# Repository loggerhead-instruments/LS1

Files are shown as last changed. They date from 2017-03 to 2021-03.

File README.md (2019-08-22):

# LS1
LS1 Snap multi-card audio recorder

## Updating Firmware

1.	Install Teensyduino from https://www.pjrc.com/teensy/loader.html
2.	Get latest hex file from appropriate repository
	https://github.com/loggerhead-instruments/LS1/blob/master/hex/LS1.2019-04-12.hex
	To download the file, right click on the Raw button and select Save As link.
3.	Connect microUSB cable to small board on bottom of main LS1 board. You may need to unscrew it. The microUSB cable will provide power to the LS1.
4.	Run the Teensy Loader program.
5.	From File Menu, select Open HEX File. Note that you may get an error saying the hex file is too large. You can ignore this message.
6.	From Operation menu, select Program (you may have to turn off automatic mode). Note you may need to do a physical reset by removing the board and shorting (connect with a paper clip or forceps) the pins circled in red.
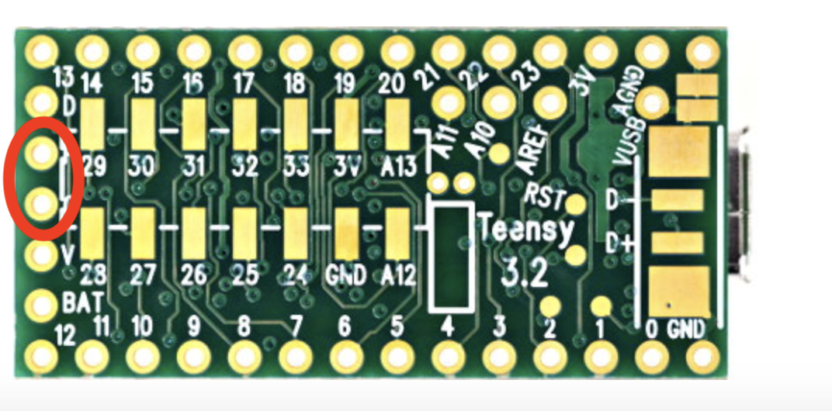
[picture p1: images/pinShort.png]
Teensy reset


To check whether the firmware has been updated, collect some data, and check the log files for the version date of the firmware.

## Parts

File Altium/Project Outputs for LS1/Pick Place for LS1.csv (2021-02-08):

Designator | Comment | Layer | Footprint | Center-Y(mm) | Center-X(mm) |  |  |  |  | X | Y | Rotation | Description
C40 | 0.01uF | BottomLayer | 402 | -50.292 | 65.913 | -27.3 | 10.6 | -27.317 | 10.584 |  |  | 270 | Ceramic Chip Capacitor - Standard
C39 | 0.01uF | BottomLayer | 402 | -14.986 | 9.652 |  |  | -62.623 | 66.845 |  |  | 360 | Ceramic Chip Capacitor - Standard
C36 | 0.01uF | BottomLayer | 402 | -34.798 | 28.702 |  |  | -42.811 | 47.795 |  |  | 360 | Ceramic Chip Capacitor - Standard
C6 | 0.01uF | BottomLayer | 402 | -37.465 | 68.326 |  |  | -40.144 | 8.171 |  |  | 270 | Ceramic Chip Capacitor - Standard
C37 | 0.1uF | BottomLayer | 402 | -50.292 | 63.881 |  |  | -27.317 | 12.616 |  |  | 270 | Ceramic Chip Capacitor - Standard
C33 | 0.1uF | BottomLayer | 402 | -17.018 | 9.652 |  |  | -60.591 | 66.845 |  |  | 360 | Ceramic Chip Capacitor - Standard
C30 | 0.1uF | BottomLayer | 402 | -36.703 | 28.702 |  |  | -40.906 | 47.795 |  |  | 360 | Ceramic Chip Capacitor - Standard
C2 | 0.1uF | BottomLayer | 402 | -37.719 | 66.421 |  |  | -39.89 | 10.076 |  |  | 270 | Ceramic Chip Capacitor - Standard
C35 | 10uF | BottomLayer | Tant0805 | -50.419 | 62.357 |  |  | -27.19 | 14.14 |  |  | 90
C31 | 10uF | BottomLayer | Tant0805 | -18.542 | 9.652 |  |  | -59.067 | 66.845 |  |  | 180
C29 | 10uF | BottomLayer | Tant0805 | -38.481 | 28.702 |  |  | -39.128 | 47.795 |  |  | 180
C1 | 10uF | BottomLayer | Tant0805 | -37.846 | 64.77 |  |  | -39.763 | 11.727 |  |  | 90
C38 | 1uF | BottomLayer | 402 | -42.799 | 64.008 |  |  | -34.81 | 12.489 |  |  | 90 | Ceramic Chip Capacitor - Standard
C34 | 1uF | BottomLayer | 402 | -16.764 | 3.175 |  |  | -60.845 | 73.322 |  |  | 90 | Ceramic Chip Capacitor - Standard
C32 | 1uF | BottomLayer | 402 | -36.322 | 22.479 |  |  | -41.287 | 54.018 |  |  | 90 | Ceramic Chip Capacitor - Standard
C4 | 1uF | BottomLayer | 402 | -31.242 | 66.421 |  |  | -46.367 | 10.076 |  |  | 360 | Ceramic Chip Capacitor - Standard
P24 | CoinCellHolder | BottomLayer | CoinCellHolder | -36.785 | 9.652 |  |  |  |  |  |  | 90
U10 | DS3231 | BottomLayer | DS3231 | -4.318 | 10.4 |  |  |  |  |  |  | 360
U9 | LP3985IM5-3.3 | BottomLayer | MF05A_N | -46.609 | 64.897 | -31 | 11.6 | -77.609 | 76.497 |  |  | 270 | Micropower, 150mA Low-Noise Ultra Low-Dropout CMOS Voltage Regulator
U8 | LP3985IM5-3.3 | BottomLayer | MF05A_N | -16.002 | 6.096 | -61.8 | 70.2 | -77.802 | 76.296 |  |  | 360 | Micropower, 150mA Low-Noise Ultra Low-Dropout CMOS Voltage Regulator
U7 | LP3985IM5-3.3 | BottomLayer | MF05A_N | -35.687 | 25.273 |  |  |  |  |  |  | 360 | Micropower, 150mA Low-Noise Ultra Low-Dropout CMOS Voltage Regulator
U1 | LP3985IM5-3.3 | BottomLayer | MF05A_N | -34.036 | 67.31 |  |  |  |  |  |  | 270 | Micropower, 150mA Low-Noise Ultra Low-Dropout CMOS Voltage Regulator
 | Header 2 | TopLayer | HDR1X2 | -63.881 | 16.891 |  |  |  |  |  |  | 180 | Header, 2-Pin
 | Header 2 | TopLayer | HDR1X2 | -61.595 | 23.368 |  |  |  |  |  |  | 180 | Header, 2-Pin
 | HYDROPHONE_MON | TopLayer | HDR1X3 | -58.674 | 31.369 |  |  |  |  |  |  | 180 | Header, 3-Pin
CAL | MJ1-3510-SMT | TopLayer | CUI_MJ1-3510-SMT | -78.197 | 8.643 |  |  |  |  |  |  | 0 | 3.5 mm, Mono, Right Angle, Surface Mount (SMT), Audio Jack Connector
R10 | 10k | TopLayer | 3-0603 | -24.765 | 17.907 |  |  |  |  |  |  | 180 | Precision Thick Film Chip Resistor, 10 Ohm to 1M Ohm Range, 1% and 0.5% Tolerance, 0603 Size, 0.063 W
R9 | 10k | TopLayer | 3-0603 | -29.718 | 18.288 |  |  |  |  |  |  | 180 | Precision Thick Film Chip Resistor, 10 Ohm to 1M Ohm Range, 1% and 0.5% Tolerance, 0603 Size, 0.063 W
R8 | 10k | TopLayer | 3-0603 | -11.303 | 9.525 |  |  |  |  |  |  | 180 | Precision Thick Film Chip Resistor, 10 Ohm to 1M Ohm Range, 1% and 0.5% Tolerance, 0603 Size, 0.063 W
R7 | 0X | TopLayer | 3-0603 | -57.023 | 15.367 |  |  |  |  |  |  | 360 | Precision Thick Film Chip Resistor, 10 Ohm to 1M Ohm Range, 1% and 0.5% Tolerance, 0603 Size, 0.063 W
P25 | Header 2 | TopLayer | HDR1X2 | -9.652 | 47.752 |  |  |  |  |  |  | 180 | Header, 2-Pin
P19 | microUSB | TopLayer | microUSB-B | -7.661 | 69.444 |  |  |  |  |  |  | 90
P18 | Header 3 | TopLayer | HDR1X3 | -79.339 | 56.4388 |  |  |  |  |  |  | 90 | Header, 3-Pin
C28 | 1.0uF | TopLayer | 402 | -67.528 | 42.47 |  |  |  |  |  |  | 360 | Ceramic Chip Capacitor - Standard
C27 | 1.0uF | TopLayer | 402 | -66.258 | 42.47 |  |  |  |  |  |  | 360 | Ceramic Chip Capacitor - Standard
U6 | MCP1700T-1802E/TT | TopLayer | SOT-23-TT3_N | -57.622 | 43.867 |  |  |  |  |  |  | 180 | Low Quiescent Current LDO, 3-Pin SOT-23, Extended Temperature, Tape and Reel
U5 | LP3985IM5-3.3 | TopLayer | MF05A_N | -63.591 | 59.996 |  |  |  |  |  |  | 180 | Micropower, 150mA Low-Noise Ultra Low-Dropout CMOS Voltage Regulator
U4 | LP3985IM5-3.3 | TopLayer | MF05A_N | -58.13 | 20.626 |  |  |  |  |  |  | 0 | Micropower, 150mA Low-Noise Ultra Low-Dropout CMOS Voltage Regulator
U3 | SGTL5000 | TopLayer | QFN32 | -62.829 | 49.709 |  |  |  |  |  |  | 360 | SGTL5000
U2 | LP3985IM5-3.3 | TopLayer | MF05A_N | -78.196 | 42.216 |  |  |  |  |  |  | 0 | Micropower, 150mA Low-Noise Ultra Low-Dropout CMOS Voltage Regulator
R6 | 10k | TopLayer | 3-0603 | -29.682 | 40.692 |  |  |  |  |  |  | 90 | Precision Thick Film Chip Resistor, 10 Ohm to 1M Ohm Range, 1% and 0.5% Tolerance, 0603 Size, 0.063 W
R5 | 10k | TopLayer | 3-0603 | -28.158 | 44.375 |  |  |  |  |  |  | 0 | Precision Thick Film Chip Resistor, 10 Ohm to 1M Ohm Range, 1% and 0.5% Tolerance, 0603 Size, 0.063 W
R4 | 10k | TopLayer | 3-0603 | -42.509 | 55.424 |  |  |  |  |  |  | 270 | Precision Thick Film Chip Resistor, 10 Ohm to 1M Ohm Range, 1% and 0.5% Tolerance, 0603 Size, 0.063 W
R3 | 10k | TopLayer | 3-0603 | -40.731 | 38.66 |  |  |  |  |  |  | 180 | Precision Thick Film Chip Resistor, 10 Ohm to 1M Ohm Range, 1% and 0.5% Tolerance, 0603 Size, 0.063 W
R2 | 100k | TopLayer | 3-0603 | -38.608 | 54.356 |  |  |  |  |  |  | 180 | Precision Thick Film Chip Resistor, 10 Ohm to 1M Ohm Range, 1% and 0.5% Tolerance, 0603 Size, 0.063 W
R1 | 100k | TopLayer | 3-0603 | -37.084 | 54.356 |  |  |  |  |  |  | 0 | Precision Thick Film Chip Resistor, 10 Ohm to 1M Ohm Range, 1% and 0.5% Tolerance, 0603 Size, 0.063 W
P17 | HYDROPHONE | TopLayer | HDR1X3 | -61.432 | 41.581 |  |  |  |  |  |  | 180 | Header, 3-Pin
P16 | HYDROPHONE | TopLayer | HDR1X3 | -61.468 | 31.369 |  |  |  |  |  |  | 180 | Header, 3-Pin
P15 | pushbutton | TopLayer | SOP4 | -18.851 | 26.573 |  |  |  |  |  |  | 0
P14 | pushbutton | TopLayer | SOP4 | -27.868 | 26.573 |  |  |  |  |  |  | 0
P13 | pushbutton | TopLayer | SOP4 | -9.707 | 26.573 |  |  |  |  |  |  | 0
P12 | Header 2 | TopLayer | HDR1X2 | -68.834 | 3.556 |  |  |  |  |  |  | 180 | Header, 2-Pin
P11 | Header 4 | TopLayer | HDR1X4 | -47.208 | 20.372 |  |  |  |  |  |  | 90 | Header, 4-Pin
P10 | Header 6 | TopLayer | HDR1X6 | -8.981 | 1.068 |  |  |  |  |  |  | 90 | Header, 6-Pin
P9 | BIG CAP 1000 uF | TopLayer | HDR1X3 | -22.098 | 15.748 |  |  |  |  |  |  | 360 | Header, 3-Pin
P8 | BIG CAP 1000 uF | TopLayer | HDR1X3 | -3.429 | 27.178 |  |  |  |  |  |  | 360 | Header, 3-Pin
P7 | microSD Hirose | TopLayer | DM3D_microSD | -48.7955 | 6.328 |  |  |  |  |  |  | 360
P6 | microSD Hirose | TopLayer | DM3D_microSD | -32.4125 | 6.328 |  |  |  |  |  |  | 360
P5 | microSD Hirose | TopLayer | DM3D_microSD | -49.5575 | 65.658 |  |  |  |  |  |  | 180
P4 | microSD Hirose | TopLayer | DM3D_microSD | -33.0475 | 65.658 |  |  |  |  |  |  | 180
P3 | Header 2 | TopLayer | HDR1X2 | -9.652 | 39.243 |  |  |  |  |  |  | 180 | Header, 2-Pin
P2 | switch | TopLayer | HDR1X3 | -0.345 | 27.23 |  |  |  |  |  |  | 180 | Header, 3-Pin
P1 | Teensy3.x | TopLayer | Teensy3.x | -29.301 | 42.597 |  |  |  |  |  |  | 180
C26 | 1uF | TopLayer | 402 | -58.13 | 41.454 |  |  |  |  |  |  | 270 | Ceramic Chip Capacitor - Standard
C25 | 10uF | TopLayer | Tant0805 | -57.749 | 47.931 |  |  |  |  |  |  | 90
C24 | 1.0uF | TopLayer | 402 | -64.099 | 35.993 |  |  |  |  |  |  | 270 | Ceramic Chip Capacitor - Standard
C23 | 1.0uF | TopLayer | 402 | -68.29 | 35.993 |  |  |  |  |  |  | 270 | Ceramic Chip Capacitor - Standard
C22 | 0.01uF | TopLayer | 402 | -60.924 | 58.218 |  |  |  |  |  |  | 180 | Ceramic Chip Capacitor - Standard
C21 | 1uF | TopLayer | 402 | -63.845 | 62.79 |  |  |  |  |  |  | 90 | Ceramic Chip Capacitor - Standard
C20 | 0.1uF | TopLayer | 402 | -63.718 | 57.075 |  |  |  |  |  |  | 90 | Ceramic Chip Capacitor - Standard
C19 | 10uF | TopLayer | Tant0805 | -63.718 | 55.551 |  |  |  |  |  |  | 270
C18 | 0.1uF | TopLayer | 402 | -66.639 | 47.027 |  |  |  |  |  |  | 180 | Ceramic Chip Capacitor - Standard
C17 | 0.01uF | TopLayer | 402 | -59.436 | 24.384 |  |  |  |  |  |  | 360 | Ceramic Chip Capacitor - Standard
C16 | 0.1uF | TopLayer | 402 | -63.591 | 54.154 |  |  |  |  |  |  | 90 | Ceramic Chip Capacitor - Standard
C15 | 1uF | TopLayer | 402 | -57.749 | 17.832 |  |  |  |  |  |  | 270 | Ceramic Chip Capacitor - Standard
C14 | 0.1uF | TopLayer | 402 | -57.404 | 23.368 |  |  |  |  |  |  | 270 | Ceramic Chip Capacitor - Standard
C13 | 10uF | TopLayer | Tant0805 | -57.404 | 25.019 |  |  |  |  |  |  | 90
C12 | 0.1uF | TopLayer | 402 | -62.448 | 46.026 |  |  |  |  |  |  | 90 | Ceramic Chip Capacitor - Standard
C11 | 0.01uF | TopLayer | 402 | -80.609 | 44.375 |  |  |  |  |  |  | 360 | Ceramic Chip Capacitor - Standard
C10 | 1uF | TopLayer | 402 | -77.942 | 39.422 |  |  |  |  |  |  | 270 | Ceramic Chip Capacitor - Standard
C9 | 0.1uF | TopLayer | 402 | -77.815 | 44.883 |  |  |  |  |  |  | 270 | Ceramic Chip Capacitor - Standard
C8 | 10uF | TopLayer | Tant0805 | -77.815 | 46.28 |  |  |  |  |  |  | 90
C7 | 0.1uF | TopLayer | 402 | -57.749 | 46.534 |  |  |  |  |  |  | 270 | Ceramic Chip Capacitor - Standard
C5 | 0.1uF | TopLayer | 402 | -5.044 | 19.61 |  |  |  |  |  |  | 180 | Ceramic Chip Capacitor - Standard
C3 | 10uF | TopLayer | Tant0805 | -3.647 | 19.61 |  |  |  |  |  |  | 0
P20 | 1x4 1.27mm | TopLayer | Header1x4_1.27mm | -50.038 | 27.051 |  |  |  |  |  |  | 360
P21 | 1x4 1.27mm | TopLayer | Header1x4_1.27mm | -44.069 | 31.115 |  |  |  |  |  |  | 90
P22 | 1x4 1.27mm | TopLayer | Header1x4_1.27mm | -44.069 | 23.368 |  |  |  |  |  |  | 90
P23 | 1x4 1.27mm | TopLayer | Header1x4_1.27mm | -44.069 | 27.305 |  |  |  |  |  |  | 90

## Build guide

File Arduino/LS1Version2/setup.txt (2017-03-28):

// Example setup.txt file

// Set time on power
TM 2016-06-06 12:00:00

// Enable IMU 100 Hz
IM 100.0

// MS Pressure
MP

// RGB light sensor
LS

// Rec duration
RD 30

// Rec interval
RI 30

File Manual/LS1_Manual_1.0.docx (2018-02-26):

# LS1/LS1X MANUAL

Multi-card Long-Term Underwater Acoustic Recorder

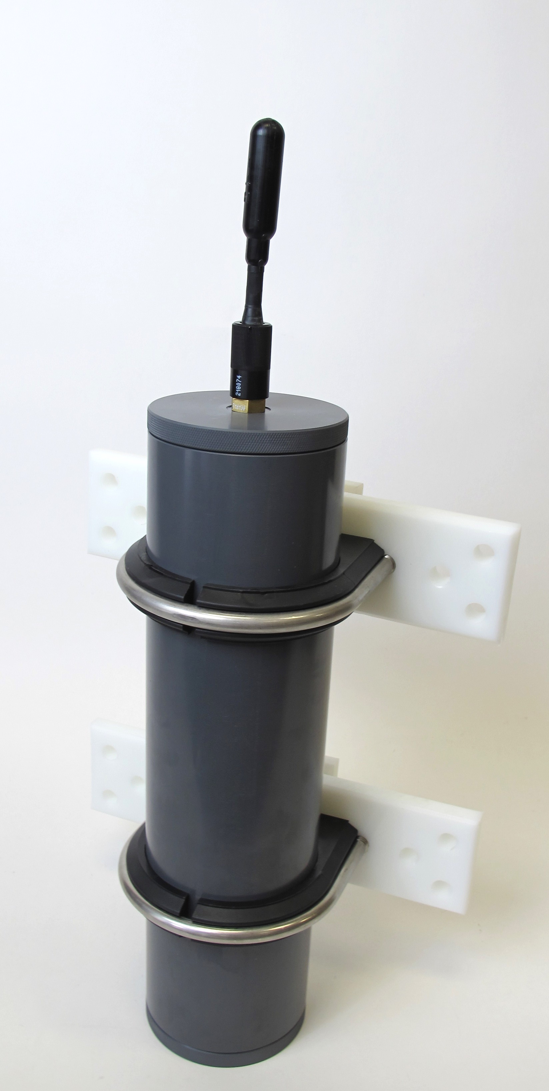
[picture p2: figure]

Manual v1.0

Updated 26 February 2018

www.loggerhead.com

# Overview

Hardware

LS1/LS1X is a multi-card datalogger designed for collecting large amounts of underwater acoustic recordings. Setup is designed to run through a simple button interface with a display. No PC is needed to setup and deploy the LS1/LS1X.

- HTI-96-min hydrophone
- Fixed 44.1 kHz sample rate
- Up to 4 microSD cards formatted as FAT32

Software

LS1/LS1X store data directly as audio wav files.

Any audio analysis software (Adobe Audition, Cornell Raven, MATLAB, R, Python) will work with these files.

Setting up LS1/LS1X for Deployment

See the online video for a tutorial on setting up the LS1/LS1X

Step 1. Prepare microSD card. Create setup.txt file if changing default gain setting. This is usually not necessary. Be sure to safely eject the card before removing from computer.

microSD cards larger than 32 GB need to be formatted as FAT32. Appendix 1 describes software that can be used to do this on Windows PCs.

Step 2. O-rings. Clean and grease o-rings with silicone grease and insert into the groove on the ring. The fatter radial o-ring is 5 mm wide x 90 mm inner diameter (McMaster Part number 9262K395 (https://www.mcmaster.com/)). The o-ring that seals with the top of the tube is -155 (McMaster Part number 9452K176 (https://www.mcmaster.com/)).

Step 3. Turn on power switch.

The microSD cards will be scanned for free memory. There MUST be a card in slot 1.

Use buttons to change settings

Enter: Used to move through menu settings and accept changes.

UP/DN: Used to change values.

Display Setting | Description
UP+DN->Rec | Hold down UP + DN to start Press Enter to change settings
Rec: | Record duration in seconds
Slp: | Sleep duration in seconds. This is the time from the END of one recording to the START of the next recording.
Batt: | Number of battery packs you will fill. There are 3 D-cells per battery pack. This setting was made available in Feb 2018. Previous versions of firmware used 4 battery packs for this setting.
Year: | Year
Month: | Month
Day: | Day of month
Hour: | Hour (24 hour time)
Minute: | Minute
Second: | Second
Mode: | Switch between Norm(al) and Diel recording. In Diel recording mode the Start HH:MM and End HH:MM are specified to limit recording to certain parts of the day (e.g. record only in the morning). In Normal recording mode, recordings are made throughout the day.

Step 5. Start Recording. Hold down the UP and DN buttons at the same time to start recording. If this is not done, the recorder will automatically start after 15 minutes.

Step 6. Close lid. Lids should be closed securely using a coin. It should be more than hand-tight.

setup.txt Commands

All commands are optional. Default column lists values if no setting in setup.txt file. Record duration and record interval can be set through the button interface.

Command | Function | Default | Example | Setup.txt example
RD | Record duration (s) | Last used | Record 600 second files | RD 600
RI | Record interval (s) | Last used | Sleep 240 seconds between files | RI 240
SG | Hydrophone system gain. See table for dB gains associated with different settings. | 4 | Set gain to setting ‘10’, which corresponds to 11.1 dB gain | SG 10
ND | Remove DC from audio. Turning on increases electrical noise | Off | Turn on feature to remove DC from audio | ND

Power

The LS1 has battery holders for 4 sets of D-cell batteries (12 batteries total).

The LS1X has battery holders for 8 sets of D-cell batteries (24 batteries total).

Always use new batteries with the LS1, and tape them into place.

The display will provide estimated run time based on the number of battery packs that are filled (LS1: 1-4 battery packs: LS1X: 1-8 battery packs) and the memory available in all of the microSD cards.

# HTI Hydrophone and Recording Gain

The LS1/LS1X uses a hydrophone manufactured by High-Tech Inc. The sensitivity of the hydrophone will be on a specification sheet included with the shipment (typically -170 dBV/uPa or -180 dBV/uPa).

The hydrophone has a red LED in the end to indicate when it is getting power. This will only be turned on during startup and recording. The hydrophone red LED will be off when sleeping.

The A/D converter gain can be changed through the setup.txt file. The default is setting 4. The setting can be changed with SG command in setup.txt. The actual setting that was used is stored to the log.txt file.

Setting | Clip Level (peak-peak) | Clip Level (peak) | Gain (dB)
0 | 3.12 | 1.56 | -3.9
1 | 2.63 | 1.315 | -2.4
2 | 2.22 | 1.11 | -0.9
3 | 1.87 | 0.935 | 0.6
4 | 1.58 | 0.79 | 2.0
5 | 1.33 | 0.665 | 3.5
6 | 1.11 | 0.555 | 5.1
7 | 0.94 | 0.47 | 6.6
8 | 0.79 | 0.395 | 8.1
9 | 0.67 | 0.335 | 9.5
10 | 0.56 | 0.28 | 11.1
11 | 0.48 | 0.24 | 12.4
12 | 0.4 | 0.2 | 14.0
13 | 0.34 | 0.17 | 15.4
14 | 0.29 | 0.145 | 16.8
15 | 0.24 | 0.12 | 18.4

Vent Plug

This plug is only to be used if there is a leak in the housing.

A leak in the housing can be dangerous because the housing will pressurize internally to the same pressure as the depth of deployment.

If there is a leak, it is critical to relieve the pressure before removing the lid, otherwise the lid could fly off.

The vent plug can be used to relieve the pressure, by turning it slowly until you start hearing air come out. Once air starts coming out, stop unscrewing and wait until air stops coming out. The vent plug is designed to stay in the endcap and safely vent air through holes machined in the plug.

Once the internal pressure has equalized, you may remove the top lid with the hydrophone. There is no need to fully remove the vent plug. Then gently retighten the vent plug. On PVC housings be very careful not to overtighten the plug, otherwise the threads in the bottom endcap may strip.

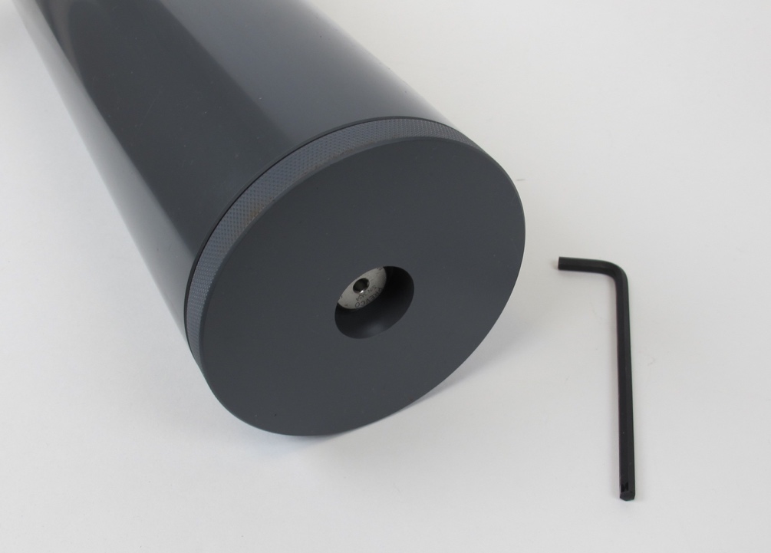
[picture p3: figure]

# Appendix I

Formatting SD card with EaseUS Partition Master for Cards Larger than 32 GB

32 GB cards can be formatted as FAT32 in Windows with standard re-formatting. New 32 GB cards will come formatted as FAT32 (you don’t need to do anything).

Cards larger than 32 GB can not be formatted with the FAT32 file system with the regular windows formatting tools. Cards shipped from Loggerhead have been formatted as FAT32. The exFAT file system will not work with the DSG boards. These larger cards can be formatted with EaseUS Partition Master, which has a free personal edition available.

http://www.partition-tool.com/personal.htm

Run EaseUS Partition Master

1. Select drive with SD card.

2. Click on Format Partition on left.

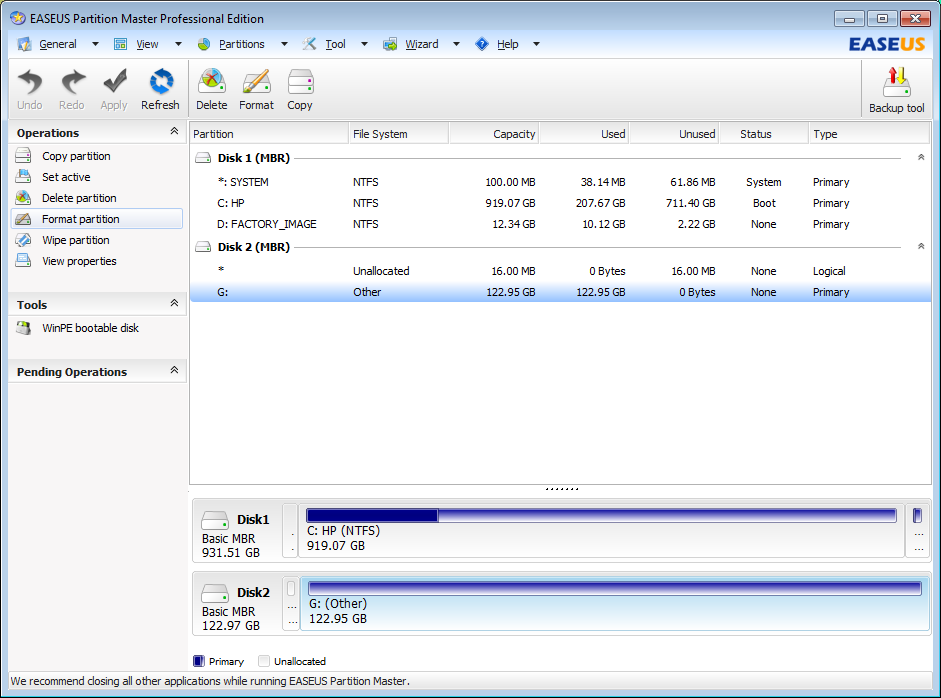
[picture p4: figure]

3. Make sure File System is FAT32. Click OK.

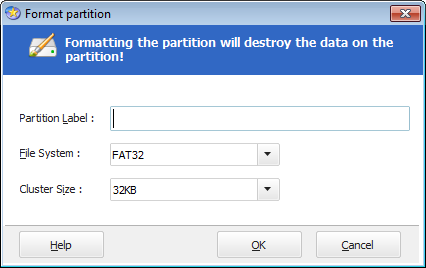
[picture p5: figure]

4. Click Apply on the toolbar. Then click Yes.

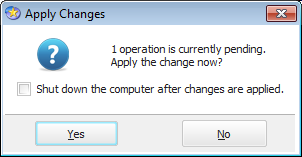
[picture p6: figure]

You should see this screen. When it is done you can close EaseUS.

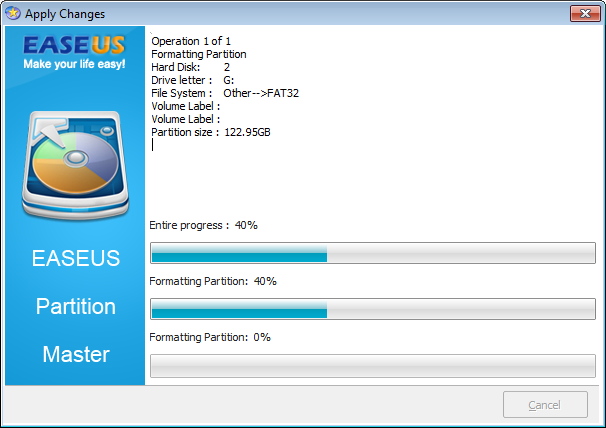
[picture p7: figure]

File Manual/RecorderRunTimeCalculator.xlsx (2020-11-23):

Record Duration (s) | Sleep Duration (s) | Sample Rate | Period (s) | Duty cycle | mA Record | mA Sleep | mAh per battery pack | battery packs | total power | Avg Power Consumption (mA) | Power Duration (h) | Power Duration (Days) | Record Duration (h) | Memory (MB) | Memory (GB)
300 | 600 | 96000 | 900 | 0.3333333333 | 50 | 3.7 | 12000 | 8 | 96000 | 19.13333333 | 5017.421603 | 209.0592334 | 1672.473868 | 1156013.937 | 1156.013937

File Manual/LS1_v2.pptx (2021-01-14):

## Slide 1

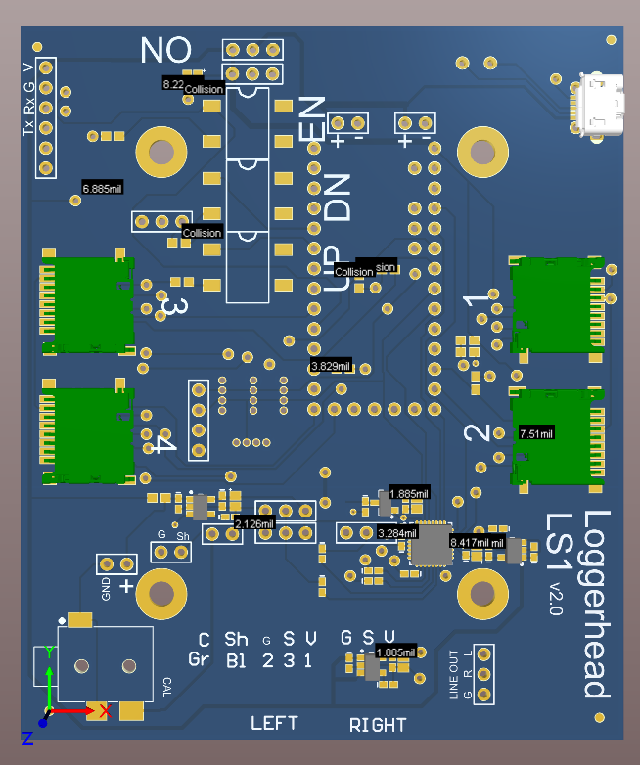
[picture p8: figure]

4

6

2

3

5

1

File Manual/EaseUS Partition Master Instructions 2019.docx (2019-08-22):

EaseUS Partition Master Instructions

https://www.easeus.com/download/epmf-download.html

1. Click on the drive with the microSD card.
2. Click Format button the right
3. In pop-up dialog box Change cluster size to 64 KB. Click OK
4. On top of screen click on Execute 1 Operation

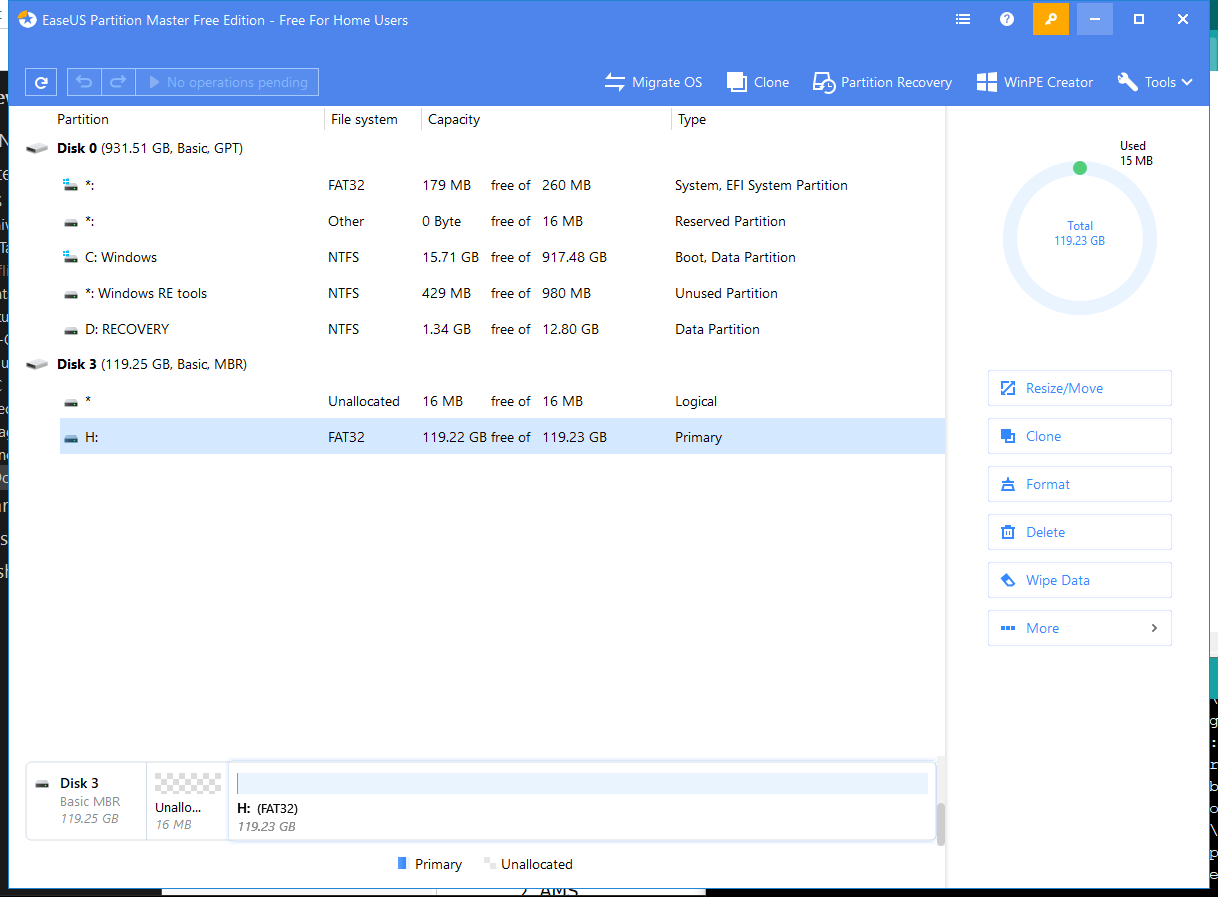
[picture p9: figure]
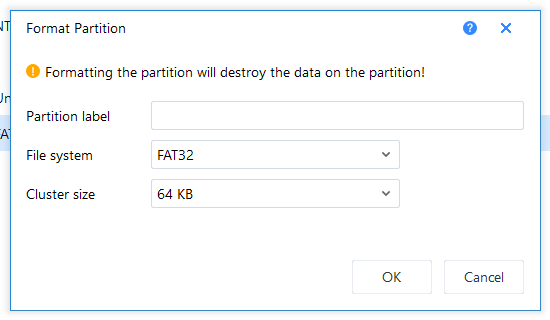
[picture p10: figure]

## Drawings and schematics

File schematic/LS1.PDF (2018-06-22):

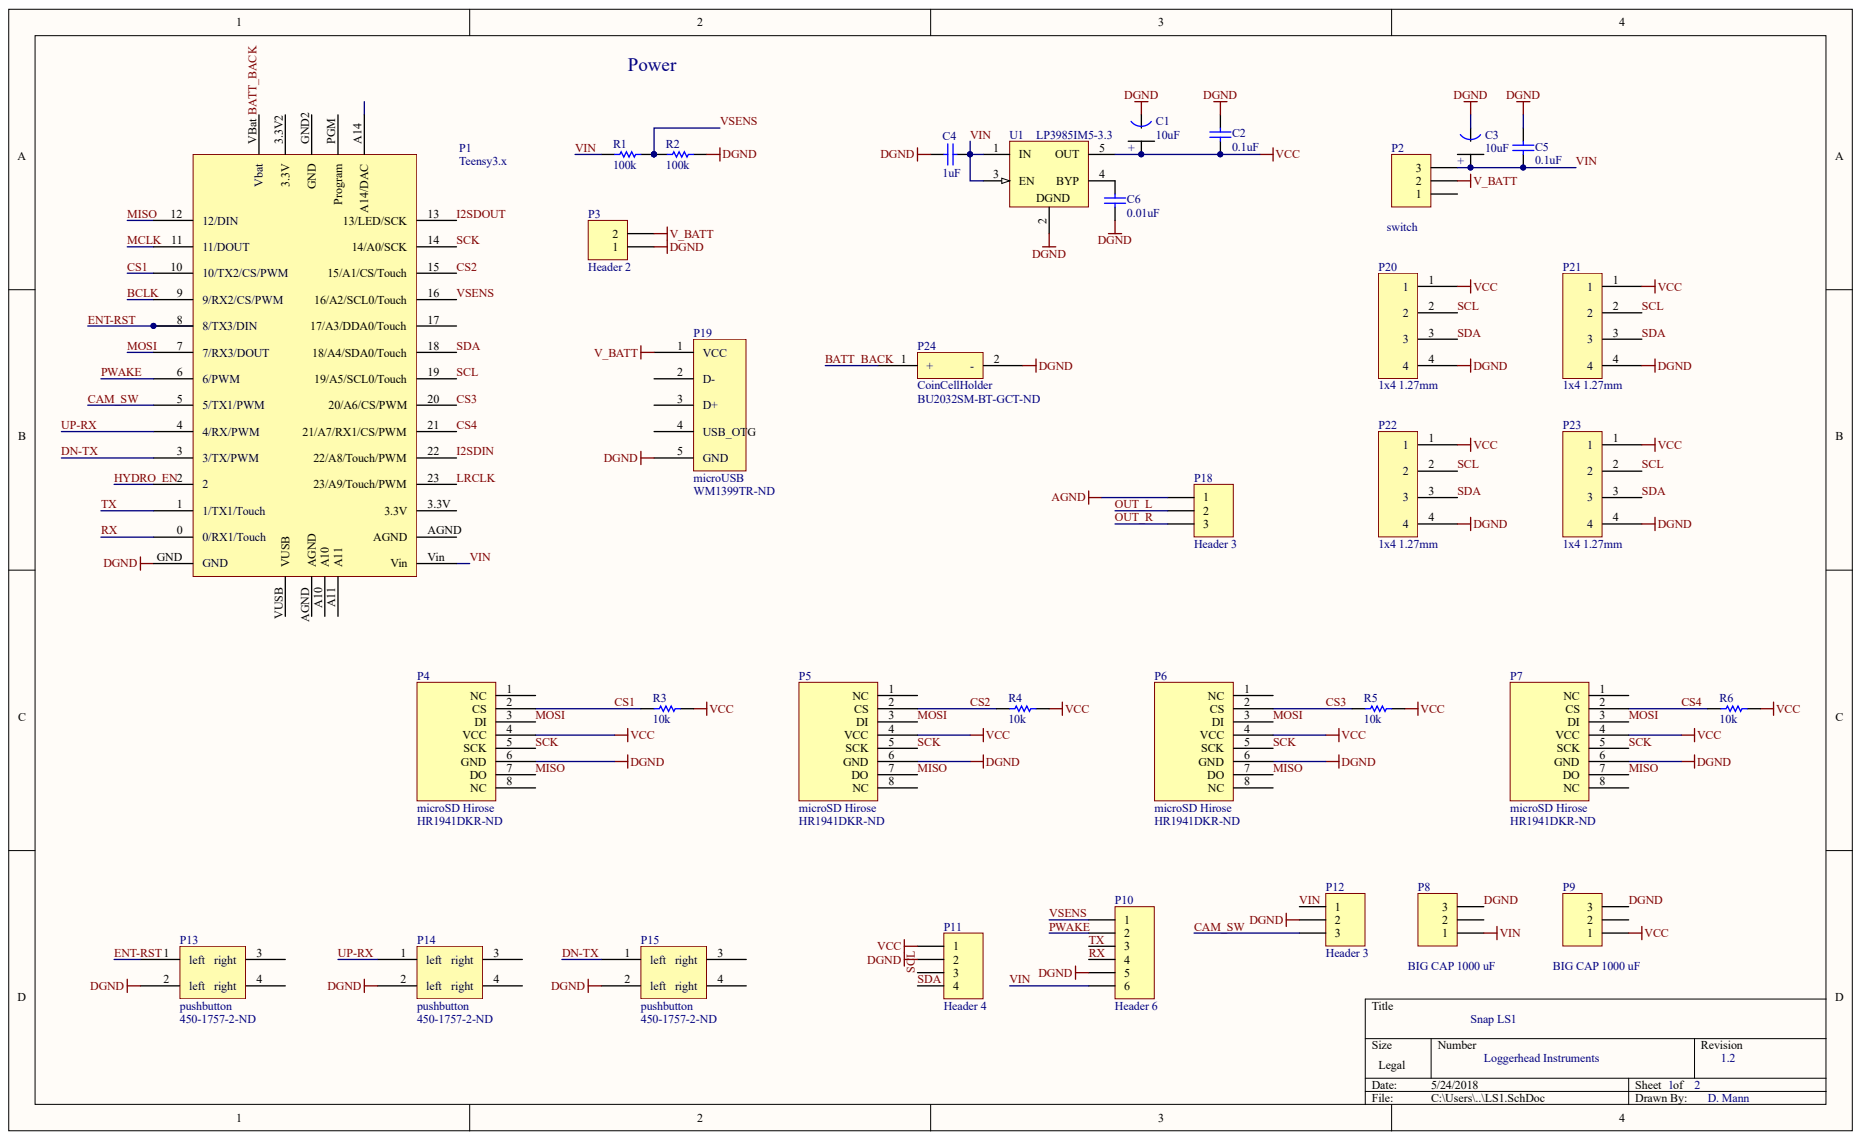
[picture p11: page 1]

Size Legal | Number Loggerhead Instruments | Revision 1.2

Date: 5/24/2018 | Sheet of 1 2
File: C:\Users\..\LS1.SchDoc | Drawn By: D. Mann

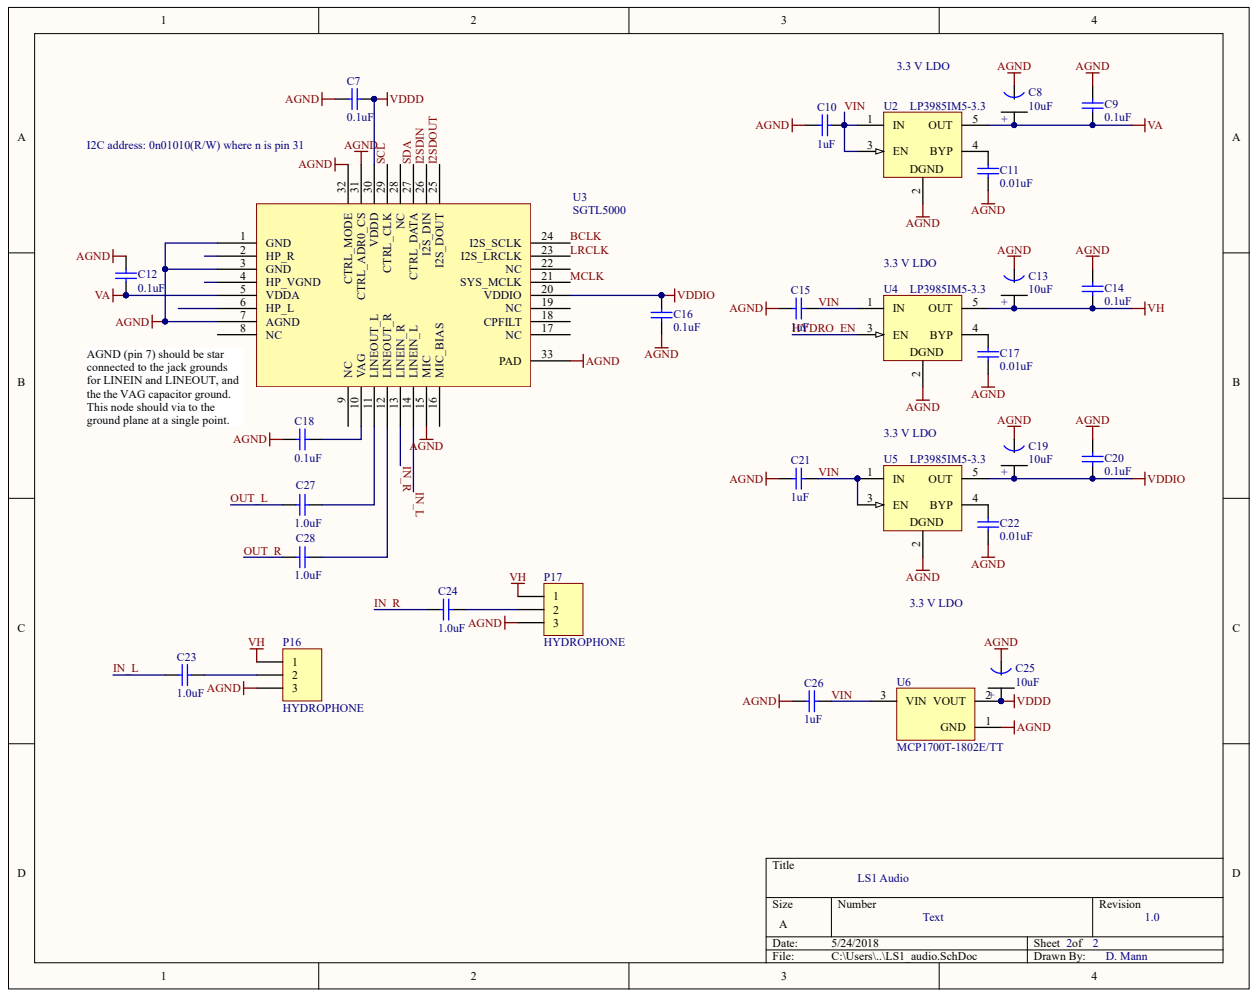
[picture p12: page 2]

AGND (pin 7) should be star
connected to the jack grounds
for LINEIN and LINEOUT, and
the the VAG capacitor ground.
This node should via to the
ground plane at a single point.

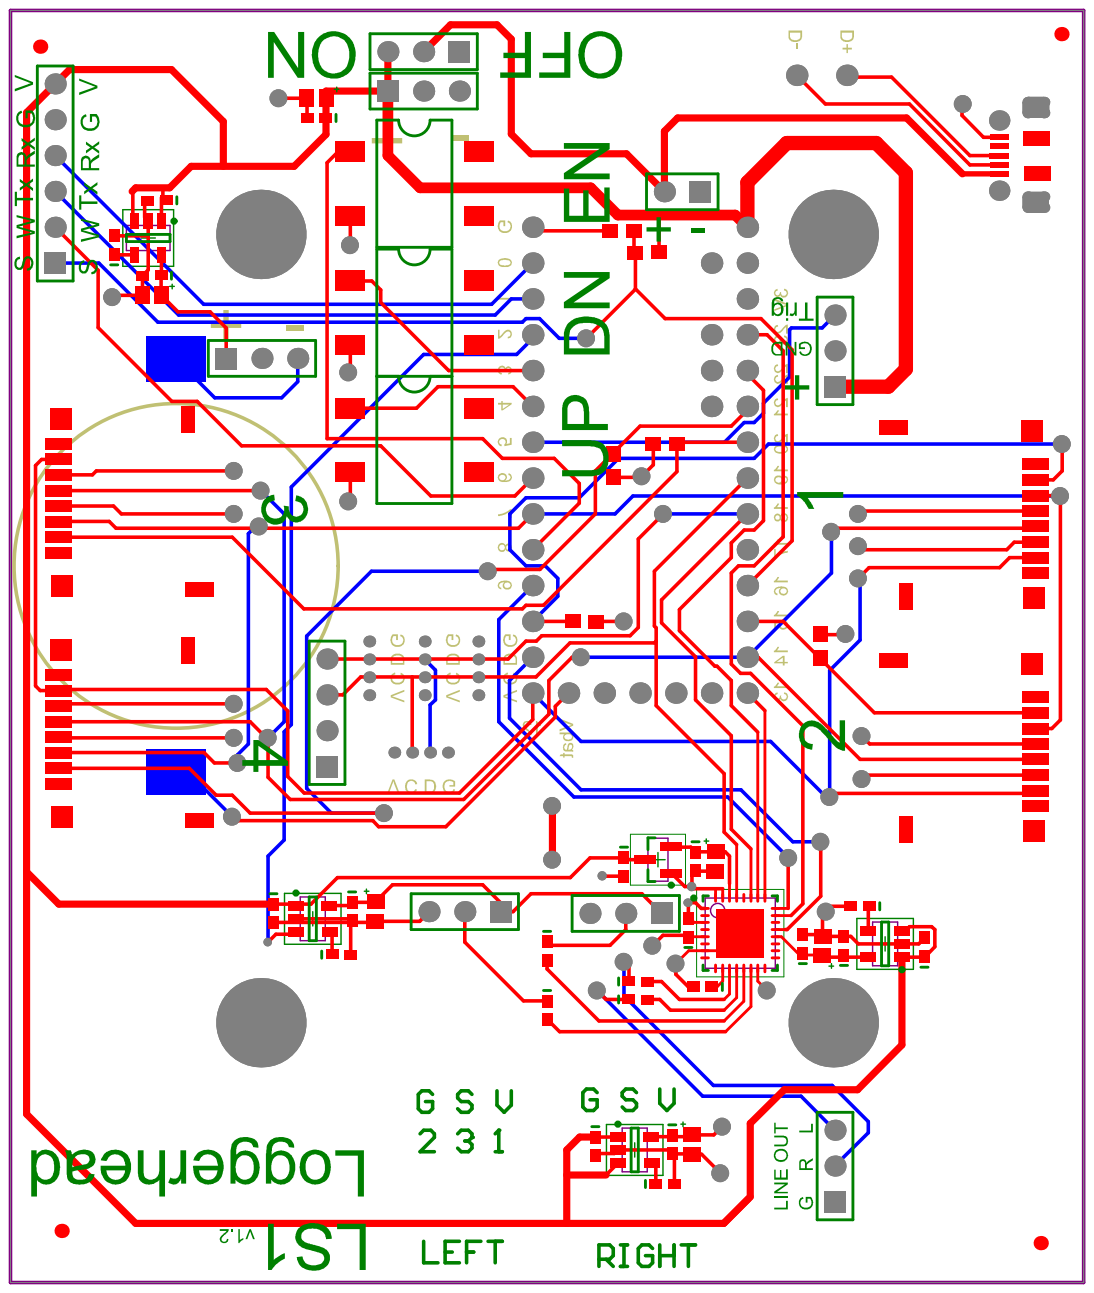
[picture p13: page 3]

Comment | Description | Designator | Footprint | LibRef | Quantity
10uF | | C1, C3, C8, C13, C19, C25 | Tant0805 | Tant0805 | 6
0.1uF | Ceramic Chip Capacitor -Standard | C2, C5, C7, C9, C12, C14, C16, C18, C20 | 0402 | C0402 | 9
1uF | Ceramic Chip Capacitor -Standard | C4, C10, C15, C21, C26 | 0402 | C0402 | 5
0.01uF | Ceramic Chip Capacitor -Standard | C6, C11, C17, C22 | 0402 | C0402 | 4
1.0uF | Ceramic Chip Capacitor -Standard | C23, C24, C27, C28 | 0402 | C0402 | 4
Teensy3.x | | P1 | Teensy3.x | Teensy3.x | 1
switch | Header, 3-Pin | P2 | HDR1X3 | Header 3 | 1
Header 2 | Header, 2-Pin | P3 | HDR1X2 | Header 2 | 1
microSD Hirose | | P4, P5, P6, P7 | DM3D microSD | microSD Hirose | 4
BIG CAP 1000 uF | Header, 3-Pin | P8, P9 | HDR1X3 | Header 3 | 2
Header 6 | Header, 6-Pin | P10 | HDR1X6 | Header 6 | 1
Header 4 | Header, 4-Pin | P11 | HDR1X4 | Header 4 | 1
Header 3 | Header, 3-Pin | P12, P18 | HDR1X3 | Header 3 | 2
pushbutton | | P13, P14, P15 | SOP4 | pushbutton | 3
HYDROPHONE | Header, 3-Pin | P16, P17 | HDR1X3 | Header 3 | 2
microUSB | | P19 | microUSB-B | microUSB-B | 1
1x4 1.27mm | | P20, P21, P22, P23 | Header1x4 1.27mm | Header 1x4 1.27mm | 4
CoinCellHolder | | P24 | CoinCellHolder | CoinCellHolder | 1
100k | Precision Thick Film Chip Resistor, 10 Ohm to 1M Ohm Range, 1% and 0.5% Tolerance, 0603 Size, 0.063 W | R1, R2 | 3-0603 | ERJ3RK | 2
10k | Precision Thick Film Chip Resistor, 10 Ohm to 1M Ohm Range, 1% and 0.5% Tolerance, 0603 Size, 0.063 W | R3, R4, R5, R6 | 3-0603 | ERJ3RK | 4
LP3985IM5-3.3 | Micropower, 150mA Low-Noise Ultra Low-Dropout CMOS Voltage Regulator | U1, U2, U4, U5 | MF05A_N | LP3985IM5-3.3 | 4
SGTL5000 | SGTL5000 | U3 | QFN32 | SGTL5000 | 1
MCP1700T-1802E/TT | Low Quiescent Current LDOU6 | | SOT-23- TT3_ N | MCP1700T-1802E/TT | 1

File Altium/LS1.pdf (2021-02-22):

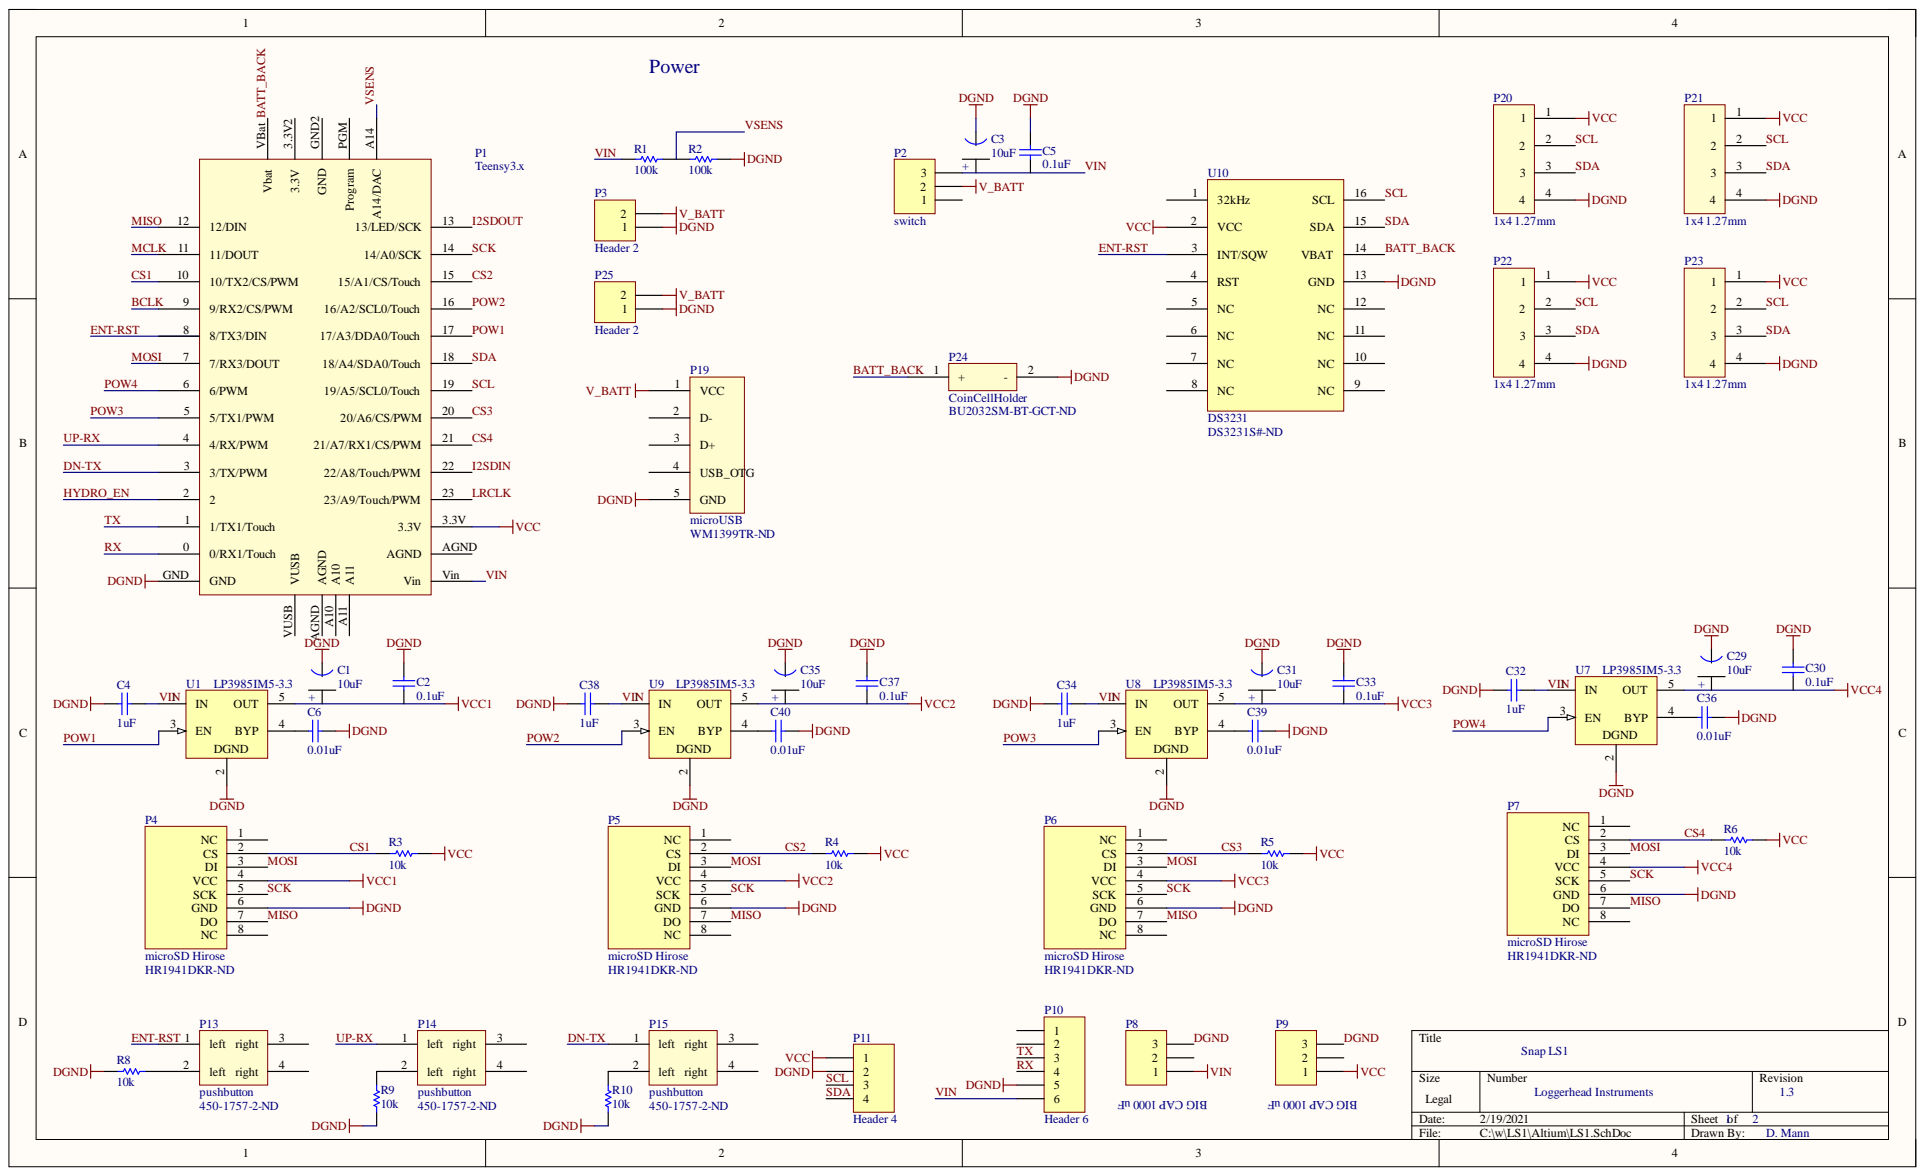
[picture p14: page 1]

Size Legal | Number Loggerhead Instruments | Revision 1.3

Date: 2/19/2021 | Sheet of 1 2
File: C:\w\LS1\Altium\LS1.SchDoc | Drawn By: D. Mann

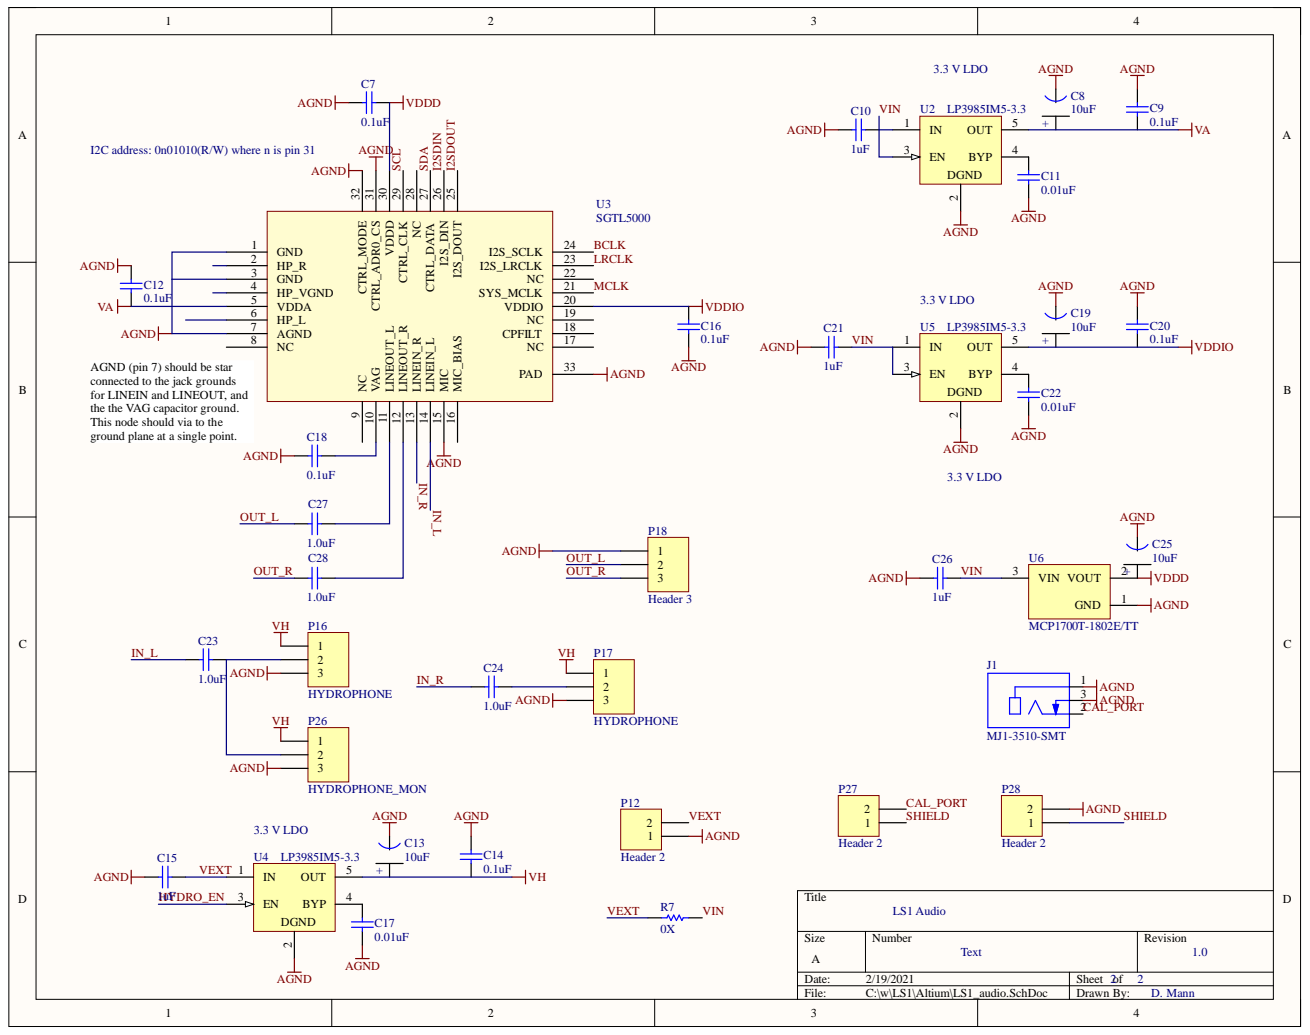
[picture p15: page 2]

AGND (pin 7) should be star
connected to the jack grounds
for LINEIN and LINEOUT, and
the the VAG capacitor ground.
This node should via to the
ground plane at a single point.

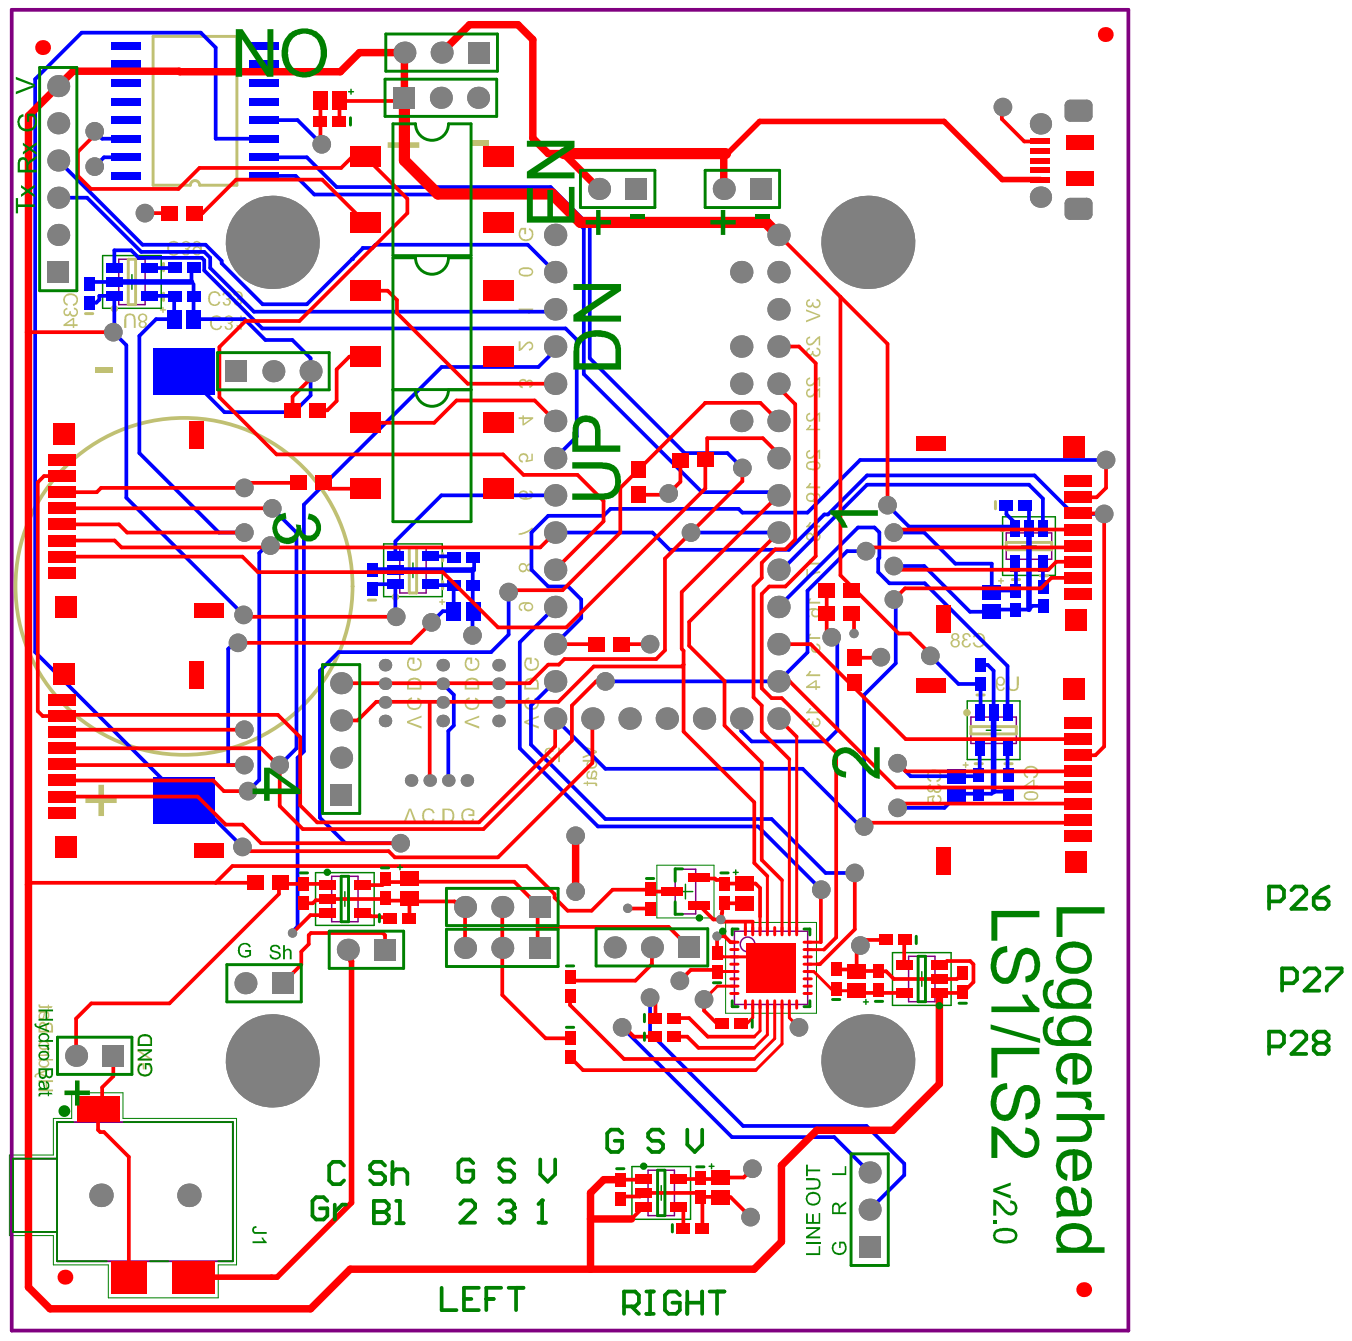
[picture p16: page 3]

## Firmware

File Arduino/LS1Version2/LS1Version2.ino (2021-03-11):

//
// LS1 acoustic recorder
//
// Loggerhead Instruments
// 2021
// David Mann

// To Do: 
// - test card switching (need to create folder when switch)
// - measure current draw 
//    - 96 MHz 48 kHz: 32 GB microSD; 46 mA record  2.8 mA sleep with microSD powered
//    - 96 MHz 48 kHz: 32 GB microSD; 46 mA record 2.6 mA sleep with microSD powered off
//    - 72 MHz 48 kHz: 32 GB microSD; 42 mA record  2.6-2.7 mA sleep with microSD powered off
//    - 72 MHz 48 kHz: 1 TB microSD; 32-44 mA (very spiky)record 3.8 mA sleep with microSD powered off (voltage regulator still shows 2.79 V when off)
//    - 72 MHz 48 kHz: 1 TB microSD; 32-44 mA (very spiky)record 3.9 mA sleep with microSD powered off, CS low, MISO/MOSI LOW. (voltage regulator still shows 2.79 V when off)

//    - 72 MHz 48 kHz: 32 GB microSD; 42 mA record 2.8 mA sleep with microSD powered off;CS low, MISO/MOSI INPUT_DISABLE. 
//    - 72 MHz 48 kHz: 1 TB microSD; 38 mA record 2.7 mA sleep with microSD powered off;CS low, MISO/MOSI INPUT_DISABLE. Shows 0.9V at LDO for uSD.
//    - 72 MHz 48 kHz: 1 TB microSD; 38 mA record 2.7 mA sleep with microSD powered off;CS low, MISO/MOSI INPUT_DISABLE. I2S input disable (new audio is zeros after sleep)

// - filenames Manta compliant
// - test continuous record
// - test 60s rec 60s sleep 1 day

// 
// Modified from PJRC audio code
// http://www.pjrc.com/store/teensy3_audio.html
//
// Compile with 72 MHz Fastest

// Modified by WMXZ 15-05-2018 for SdFS and multiple sampling frequencies
// Optionally uses SdFS from Bill Greiman https://github.com/greiman/SdFs; but has higher current draw in sleep

//*****************************************************************************************

char codeVersion[12] = "2021-03-09";
static boolean printDiags = 0;  // 1: serial print diagnostics; 0: no diagnostics
#define USE_SDFS 0  // to be used for exFAT but works also for FAT16/32
#define MQ 100 // to be used with LHI record queue (modified local version)
int roundSeconds = 60;//start time modulo to nearest roundSeconds
int wakeahead = 5;  //wake from snooze to give hydrophone time to power up
int noDC = 0; // 0 = freezeDC offset; 1 = remove DC offset; 2 = bypass
//*****************************************************************************************


#include "LHI_record_queue.h"
#include "control_sgtl5000.h"

//#include <SerialFlash.h>
#if USE_SDFS==0
  #include "input_i2s.h"
//  #include "LHI_record_queue.h"
//  #include "control_sgtl5000.h"
#else
  #include <Audio.h>  //this also includes SD.h from lines 89 & 90
#endif
#include <Wire.h>
#include <SPI.h>
#if USE_SDFS==1
  #include "SdFs.h"
#else
  #include "SdFat.h"
#endif
#include "amx32.h"

#include <Snooze.h>  //using https://github.com/duff2013/Snooze; uncomment line 62 #define USE_HIBERNATE

#include <TimeLib.h>
#include <Adafruit_GFX.h>
#include <Adafruit_SSD1306.h>
#include <EEPROM.h>
//#include <TimerOne.h>

#define CPU_RESTART_ADDR (uint32_t *)0xE000ED0C
#define CPU_RESTART_VAL 0x5FA0004
#define CPU_RESTART (*CPU_RESTART_ADDR = CPU_RESTART_VAL);

#define OLED_RESET -1
Adafruit_SSD1306 display(OLED_RESET);
#define BOTTOM 55

// set this to the hardware serial port you wish to use
#define HWSERIAL Serial1

#define NREC 32 // increase disk buffer to speed up disk access

static uint32_t myID[2];
unsigned long baud = 115200;

#define SECONDS_IN_MINUTE 60
#define SECONDS_IN_HOUR 3600
#define SECONDS_IN_DAY 86400
#define SECONDS_IN_YEAR 31536000
#define SECONDS_IN_LEAP 31622400

#define MODE_NORMAL 0
#define MODE_DIEL 1

// GUItool: begin automatically generated code
AudioInputI2S            i2s2;           //xy=105,63
LHIRecordQueue           queue1;         //xy=281,63
AudioConnection          patchCord1(i2s2, 0, queue1, 0);
AudioControlSGTL5000     sgtl5000_1;     //xy=265,212
// GUItool: end automatically generated code

const int myInput = AUDIO_INPUT_LINEIN;
int gainSetting = 4; //default gain setting; can be overridden in setup file


// Pin Assignments
const int UP = 4;
const int DOWN = 3;
const int SELECT = 8; // pin shared with Interrupt from DS3231 RTC
const int hydroPowPin = 2;
const int vSense = A14; 

// microSD chip select pins
#define CS1 10
#define CS2 15
#define CS3 20
#define CS4 21
#define SDPOW1 17
#define SDPOW2 16
#define SDPOW3 5
#define SDPOW4 6
int chipSelect[4];
int sdPowSelect[4];
uint32_t freeMB[4];
uint32_t filesPerCard[4];
int currentCard = 0;
boolean newCard = 0;

// Pins used by audio shield
// https://www.pjrc.com/store/teensy3_audio.html
// MEMCS 6
// MOSI 7
// BCLK 9
// SDCS 10
// MCLK 11
// MISO 12
// RX 13
// SCLK 14
// VOL 15
// SDA 18
// SCL 19
// TX 22
// LRCLK 23

// Remember which mode we're doing
int mode = 0;  // 0=stopped, 1=recording, 2=playing
time_t startTime;
time_t stopTime;
time_t t;

byte startHour, startMinute, endHour, endMinute; //used in Diel mode
long dielRecSeconds;

boolean audioFlag = 1;

boolean LEDSON=1;
boolean introperiod=1;  //flag for introductory period; used for keeping LED on for a little while

int32_t lhi_fsamps[7] = {8000, 16000, 32000, 44100, 48000, 96000, 192000};
#define I_SAMP 6   // 0 is 8 kHz; 1 is 16 kHz; 2 is 32 kHz; 3 is 44.1 kHz; 4 is 48 kHz; 5 is 96 kHz; 6 is 192 kHz

float audio_srate = lhi_fsamps[I_SAMP];//44100.0;
int isf = I_SAMP;

//WMXZ float audioIntervalSec = 256.0 / audio_srate; //buffer interval in seconds
//WMXZ unsigned int audioIntervalCount = 0;
float gainDb;

int recMode = MODE_NORMAL;
long rec_dur = 10;
long rec_int = 30;

int snooze_hour;
int snooze_minute;
int snooze_second;
int buf_count;
long nbufs_per_file;
boolean settingsChanged = 0;

long file_count;
char filename[60];
char dirname[20];
int folderMonth;

SnoozeAlarm alarm;
SnoozeAudio snooze_audio;
SnoozeBlock config_teensy32(snooze_audio, alarm);


// The file where data is recorded
#if USE_SDFS==1
  FsFile frec;
  SdFs sd;
#else
  File frec;
  SdFat sd;
  //SdFile file; // not used(WMXZ)
#endif

typedef struct {
    char    rId[4];
    unsigned int rLen;
    char    wId[4];
    char    fId[4];
    unsigned int    fLen;
    unsigned short nFormatTag;
    unsigned short nChannels;
    unsigned int nSamplesPerSec;
    unsigned int nAvgBytesPerSec;
    unsigned short nBlockAlign;
    unsigned short  nBitsPerSamples;
    char    dId[4];
    unsigned int    dLen;
} HdrStruct;

HdrStruct wav_hdr;

unsigned char prev_dtr = 0;


void setup() {
  read_myID();

  chipSelect[0] = CS1;
  chipSelect[1] = CS2;
  chipSelect[2] = CS3;
  chipSelect[3] = CS4;
  sdPowSelect[0] = SDPOW1;
  sdPowSelect[1] = SDPOW2;
  sdPowSelect[2] = SDPOW3;
  sdPowSelect[3] = SDPOW4;
  
  Serial.begin(baud);
  delay(500);

  RTC_CR = 0; // disable RTC
  delay(100);
  // change capacitance to 26 pF (12.5 pF load capacitance)
  RTC_CR = RTC_CR_SC16P | RTC_CR_SC8P | RTC_CR_SC2P; 
  delay(100);
  RTC_CR = RTC_CR_SC16P | RTC_CR_SC8P | RTC_CR_SC2P | RTC_CR_OSCE;
  delay(100);
  Serial.println(RTC_TSR);
  delay(1000);
  Serial.println(RTC_TSR);
  delay(1000);
  Serial.println(RTC_TSR);
  
  Wire.begin();
  pinMode(vSense, INPUT);
  analogReference(DEFAULT);
  pinMode(hydroPowPin, OUTPUT);
  digitalWrite(hydroPowPin, HIGH);
  pinMode(SDPOW1, OUTPUT);
  pinMode(SDPOW2, OUTPUT);
  pinMode(SDPOW3, OUTPUT);
  pinMode(SDPOW4, OUTPUT);
  digitalWrite(SDPOW1, LOW); // start all cards switched off in case of reset
  digitalWrite(SDPOW2, LOW);
  digitalWrite(SDPOW3, LOW);
  digitalWrite(SDPOW4, LOW);

  //setup display and controls
  pinMode(UP, INPUT_PULLUP);
  pinMode(DOWN, INPUT_PULLUP);
  pinMode(SELECT, INPUT_PULLUP);

  display.begin(SSD1306_SWITCHCAPVCC, 0x3C);  //initialize display
  delay(140);
  cDisplay();
  display.println("Loggerhead");
  display.display();
  
  // Audio connections require memory, and the record queue
  // uses this memory to buffer incoming audio.
  // initialize now to estimate DC offset during setup
  AudioMemory(MQ+10);
  
  audio_srate = lhi_fsamps[isf];
//WMXZ  audioIntervalSec = 256.0 / audio_srate; //buffer interval in seconds

  AudioInit(isf); // load current gain setting
  manualSettings();
  audio_srate = lhi_fsamps[isf];
  AudioInit(isf); // set with new settings
  logFileHeader();
  cDisplay();

  if(rec_int > 60) roundSeconds = 60;
  if(rec_int > 300) roundSeconds = 300;
  
  t = getTeensy3Time(1);  // sync teensy rtc to DS3231

  startTime = t;
  //startTime = getTeensy3Time(0);
  startTime -= startTime % roundSeconds;  
  startTime += roundSeconds; //move forward
  stopTime = startTime + rec_dur;  // this will be set on start of recording

  if (recMode==MODE_DIEL) setDielTime();  // adjust start time to diel mode
  
  nbufs_per_file = (long) (ceil(((rec_dur * audio_srate / 256.0) / (float) NREC)) * (float) NREC);
  long ss = rec_int - wakeahead;
  if (ss<0) ss=0;
  snooze_hour = floor(ss/3600);
  ss -= snooze_hour * 3600;
  snooze_minute = floor(ss/60);
  ss -= snooze_minute * 60;
  snooze_second = ss;
  Serial.print("Snooze HH MM SS ");
  Serial.print(snooze_hour);
  Serial.print(snooze_minute);
  Serial.println(snooze_second);

  Serial.print("rec dur ");
  Serial.println(rec_dur);
  Serial.print("rec int ");
  Serial.println(rec_int);
  Serial.print("Current Time: ");
  printTime(t);
  Serial.print("Start Time: ");
  printTime(startTime);
  
  // Sleep here if won't start for 60 s
  long time_to_first_rec = startTime - t;
  Serial.print("Time to first record ");
  Serial.println(time_to_first_rec);
  
  mode = 0;

  // create first folder to hold data
  folderMonth = -1;  //set to -1 so when first file made will create directory
  checkSD();
}

//
// MAIN LOOP
//

int recLoopCount;  //for debugging when does not start record
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

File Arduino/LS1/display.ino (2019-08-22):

float mAmpRec = 49;
float mAmpSleep = 3.4;
float mAmpCam = 700;
byte nBatPacks = 4;
float mAhPerBat = 12000.0; // assume 12Ah per battery pack; good batteries should be 14000

csd_t m_csd;


/* DISPLAY FUNCTIONS
 *  
 */

time_t autoStartTime;
 
void printDigits(int digits){
  // utility function for digital clock display: prints preceding colon and leading 0
  display.print(":");
  printZero(digits);
  display.print(digits);
}

void printZero(int val){
  if(val<10) display.print('0');
}

#define noSet 0
#define setRecDur 1
#define setRecSleep 2
#define setYear 3
#define setMonth 4
#define setDay 5
#define setHour 6
#define setMinute 7
#define setSecond 8
#define setFsamp 9
#define setBatPack 10
#define setMode 11
#define setStartHour 12
#define setStartMinute 13
#define setEndHour 14
#define setEndMinute 15


void manualSettings(){
  boolean startRec = 0, startUp, startDown;
  readEEPROM();
  calcGain();

  autoStartTime = getTeensy3Time();

// get free space on cards
    cDisplay();
    display.print("LS1 Init");
    display.setTextSize(1);
    display.setCursor(0, 16);
    display.println("Card Free/Total MB");
    // Initialize the SD card
    SPI.setMOSI(7);
    SPI.setSCK(14);
    SPI.setMISO(12);
      
    for (int n=0; n<4; n++){
      freeMB[n] = 0; //reset
      Serial.println(); Serial.println();
      Serial.print("Card:"); Serial.println(n + 1);
      display.print(n + 1); display.print("    ");
      display.display();

      if(sd.begin(chipSelect[n], SD_SCK_MHZ(50))){

        int32_t volFree = sd.vol()->freeClusterCount();
        Serial.print("volFree:");
        Serial.println(volFree);

        float fs = 0.000512 * volFree * sd.vol()->blocksPerCluster();

        uint32_t freeSpace = (uint32_t) fs;
        uint32_t volumeMB = uint32_t ( 0.000512 * (float) sd.card()->cardSize());

        Serial.print("Volume MB ");
        Serial.println(volumeMB);
        
        if (freeSpace < 200) freeMB[n] = 0;
        else
          freeMB[n] = freeSpace - 200; // take off 200 MB to be safe

        Serial.print("Free space (MB): ");
        Serial.println((uint32_t) freeMB[n]);
        
        display.print(freeMB[n]);
        display.print("/");
        display.println(volumeMB);
        display.display();
        delay(1000);
      }
      else{
        Serial.println("Unable to access the SD card");
        //Serial.println(card.errorCode());
       // Serial.println(card.errorData());
        display.println("  None");
        display.display();
    }
  }

  // set back to card 1
  if(!sd.begin(chipSelect[0], SD_SCK_MHZ(50))){
    display.print("Card 1 Fail");
    display.display();
    while(1);
  }

 
  LoadScript(); // secret settings accessible from card 1
  calcGain();
  writeEEPROM(); // update EEPROM in case any settings changed from card

    // make sure settings valid (if EEPROM corrupted or not set yet)
  
  if (rec_dur < 0 | rec_dur>100000) {
    rec_dur = 60;
    writeEEPROMlong(0, rec_dur);  //long
  }
  if (rec_int<0 | rec_int>100000) {
    rec_int = 60;
    writeEEPROMlong(4, rec_int);  //long
  }
  if (startHour<0 | startHour>23) {
    startHour = 0;
    EEPROM.write(8, startHour); //byte
  }
  if (startMinute<0 | startMinute>59) {
    startMinute = 0;
    EEPROM.write(9, startMinute); //byte
  }
  if (endHour<0 | endHour>23) {
    endHour = 0;
    EEPROM.write(10, endHour); //byte
  }
  if (endMinute<0 | endMinute>59) {
    endMinute = 0;
    EEPROM.write(11, endMinute); //byte
  }
  if (recMode<0 | recMode>1) {
    recMode = 0;
    EEPROM.write(12, recMode); //byte
  }
  if (isf<0 | isf>=I_SAMP) {
    isf = I_SAMP; // change 3 to 4 to allow 192 kHz
    EEPROM.write(13, isf); //byte
  }
  if (nBatPacks<0 | nBatPacks>8){
    nBatPacks = 8;
    EEPROM.write(14, nBatPacks); //byte
  }
  if (gainSetting<0 | gainSetting>15) {
    gainSetting = 4;
    EEPROM.write(15, gainSetting); //byte
  }
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

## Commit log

2017-03-28 camera support
2017-04-19 wake ahead earlier so camera has time to turn on
2017-05-05 fix camera button timing
2017-05-10 pin 1 control bright LED
2017-05-10 brite LED control to pin 0
2017-09-26 display camera status. function to bypass ADC hp
2017-10-24 script to enable no DC circuit
2017-10-25 header for log file. wait to freeze ADC filter
2018-02-26 number of bat packs as setting
    - write/read battery packs to EEPROM
    - calculate power as nBatPacks * mAhPerBat
    - write code version to Log file
2018-03-23 shut down camera if low power
2018-03-24 voltage adjustment
    separate voltage for shutting down camera
    Note: voltage measurement is not very reliable
    fudgeFactor makes it approximately accurate around 3.5V
2018-03-24 adjust voltage thresholds
2018-05-10 update hex for low power SD firmware
2018-07-19 Leave buttons as inputs
    May cause short in Teensy if hold down button after changed to output
2018-07-31 asm("wfi"); // reduce power between interrupts
2018-09-18 camera control
2018-09-25 update current draw and code date
2018-10-16 hex: fix sample rate, add 192 kHz experimental
2018-11-20 default to disable ADC HP filter
    user can set to enable HPF or use freeze mode.
    Note, freeze mode generates high frequency noise that changes depending on the input (worst when there is no signal)
2018-11-22 default to NoDC and try to power up audio like on reset
    Do not seem to get noise band (14 kHz at 48 kHz sample rate) on first recording. And then it may alternate between sleep cycles.
    Seems to resolve when use ADC HPF and reset power at start.
2018-11-22 testing bypass ADC HPF
    ADC high-pass filter more regularly had noise
2019-04-09 Fix current surge on UP button
2019-04-10 add display power pin
2019-06-11 reset if recover from low battery
2019-06-27 camera diel record mode
    Camera only records during diel period.
    Audio records on continuous schedule
2019-08-15 camera fixes
    Start record when normal mode
    Run camera properly in diel mode with continous recording
2019-08-16 camera diel mode
    If rec interval = 0; audio and camera both run on diel mode settings
    If rec interval>0; audio runs all the time; camera follows diel mode settings
2019-08-16 fix camera diel record
2019-08-22 updated EaseUS
    [RecorderRunTimeCalculator.xlsx]
2020-12-08 Version 2
    [LS1.PcbDoc, LS1.PrjPCB, LS1.SchDoc, LS1_audio.SchDoc]
2021-01-14 add cal input and regulator for each sd
    [LS1.PcbDoc, LS1.PrjPCB, LS1_audio.SchDoc]
2021-01-18 adjust part placement
    [LS1.PcbDoc]
2021-01-19 SGTL5000 AGND to pin 3
    [LS1.PcbDoc]
2021-02-08 altium update
    [LS1.PrjPCB, LS1.SchDoc, Pick Place for LS1.csv, Pick Place for LS1.xlsx]
2021-02-08 sync teensy RTC every new file
2021-02-22 LS1 v2.1
    [LS1.PcbDoc, LS1.PrjPCB, LS1.SchDoc, LS1_audio.SchDoc]
2021-03-09 power down microSD when sleeping
2021-03-09 update pcb gerber
    [LS1.PcbDoc, LS1.PrjPCB]
2021-03-10 do not power down microSD when sleeping
2021-03-14 leave cards powered on
